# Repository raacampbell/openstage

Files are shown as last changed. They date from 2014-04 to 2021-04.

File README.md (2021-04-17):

<h1>OpenStage</h1>
<i>Open source microscope stage controller</i>
<br />

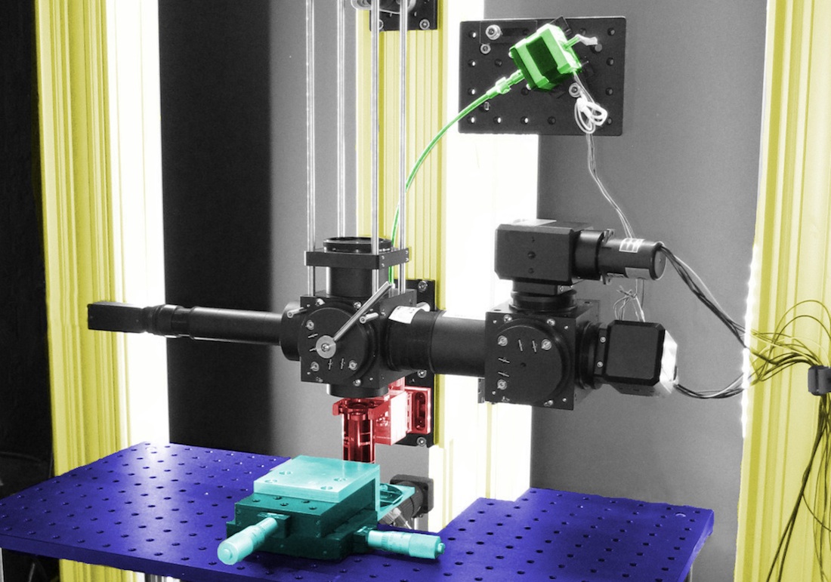
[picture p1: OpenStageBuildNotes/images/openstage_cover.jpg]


OpenStage is a hardware and software solution for cheaply motorizing a microscope stage. The system is accurate enough even for demanding tasks, such as fine focus operations on a 2-photon microscope. The characteristics of the system and important build information are described in our <a href="http://www.plosone.org/article/info%3Adoi%2F10.1371%2Fjournal.pone.0088977">PlosONE paper</a>. We achieved absolute unidirectional positioning accuracy and repeatability better than 0.1 μm in Z. Bidirectional positioning accuracy is in the range of 0.5 μm to 0.75 μm in Z. Positioning repeatability in X and Y is better than 1 μm. Minimum incremental motion is 0.04 μm in Z and 0.1 μm in X and Y. These values compare favorably to many commercial actuators costing several times as much as our system.

Our system costs roughly $1000 for three axes (controller + motors + motor coupling hardware). Up to four axes are possible. Commercial solutions cost in the region of $5,000 to $10,000. None of these costs include structural components such as bread-boards, linear translation stages, construction posts, etc, since all of this hardware is required no matter what motor solution is used. The breakdown of the costs is as follows:

* Motors and couplers are $100 to $200 per axis.
* Costs for micrometers, which act as the gear mechanism, are $80 to $150 per axis.
* A 4 axis controller unit can be assembled for under $500.

The cost savings come from the fact that we are using regular stepper motors instead of expensive linear actuators or servos. Further, the gears in our system are micrometers, which are easy to source and can even be bought at a discount from E-Bay. The main trade off compared to commercial systems is bulk, since connecting a stepper motor to a micrometer requires a relatively long (at least 8" or so) flexible shaft. However, if you can find a suitable leadscrew or rack and pinion gear as a substitute for the micrometer then the system will become more compact. A second trade off is that the controller unit does not have a feedback mechanism (encoders) for tracking position; position is inferred by counting the number of steps taken by the motors. In practice, this is not an issue as a properly assembled stage that is not driven beyond its operating limits will not lose position. Our system has maintained very high accuracy with zero maintanance. 

The stand-alone controller is based around an Arduino Mega. You can also build a single-axis controller around an Arduino Uno for under $100, but this can't accept a PS3 gamepad as there isn't sufficient SRAM on this device. The controller communicates with a PC via serial or virtual serial (USB) ports. An external LCD display and hand-held controller can also, optionally, be added. There is a PCB into which all components can easiliy be connected. The PCB was redesigned in Dec 2020 so that it's possible to construct it without obsolete SparkFun parts.  This verision of the PCB <a href="https://oshpark.com/shared_projects/8WlR0lh0">here</a> is no longer current. 

## Citing and Contact
Please do get in touch if you find this project useful or have used it in a publication. I'd love to hear from you!

## Updates

* *Arduino Mega ADK* - Users report that if the <a href="https://www.arduino.cc/en/Main/ArduinoBoardMegaADK">Arduino Mega ADK</a> is used, the project will run out of the box without the USB host shield.
* [Bluetooth gamepad connection details](https://github.com/raacampbell/openstage/issues/11#issuecomment-300612226)

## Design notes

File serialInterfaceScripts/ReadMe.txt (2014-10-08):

MATLAB and Python code examples for controlling OpenStage using the serial port commands. 

2014/04/08
Add *simple* LabVIEW VI for moving the stage.

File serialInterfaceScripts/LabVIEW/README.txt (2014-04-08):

This is a *very simple* LabVIEW VI for moving stage. Needs to be
expanded in order to become truly useful. Only sets a
position. Doesn't read one back.

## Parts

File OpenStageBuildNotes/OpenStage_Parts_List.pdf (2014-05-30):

* OpenStage PCBs can be manufactured relatively cheaply by SeeedStudio or OSH Park. Seeed has a minimum order of 5 units and OSH a minimum of 3. Seeed works out slightly cheaper in absolute terms and much cheaper per board. Listed price is roughly the cost for one OSH board. We may have boards in stock or may be able to split costs with you. If not, you're looking at around $120 to $170 for the minimum
bulk purchase.
TOTAL | 296.492
Description | Purpose | Quantity | Price Each (USD) | Sub-Total | Supplier | Part ID | | In addition, you will need a PSU that is suitable for driving your motors. It should be between 11V to 30V. Some possibilities are listed below.
Custom OpenStage PCB* | Main board | 1 | 50 | 50 | Seeedstudio or OSH Park
CUI V7809-1000 DC/DC Regulat | Produce 9V 1A DC | 1 | 7.81 | 7.81 | Digi-Key | 102-1717-ND
10uF 16V Cap | Filter for regulator | 1 | 0.48 | 0.48 | Digi-Key | 587-1376-1-ND | | Name & specs | Supplier | Part ID
10uF 50V Cap | Filter for regulator | 1 | 0.94 | 0.94 | Digi-Key | 587-3167-1-ND | | Mean Well 24V 4A. Will need jack. About $60 | Mouser | 709-CLG100-24
| | | | | | | | CUI Inc. 24V 2.7A. About $17 | Digikey | T1121-P5P-ND
5k Trim pot | LCD contrast | 1 | 0.98 | 0.98 | Digi-Key | 3362U-502LF-ND
Female DB9 connector | Motor connections | 2 | 3.14 | 6.28 | Digi-Key | 609-1485-ND
Male DB9 | PC serial port connection | 1 | 2.87 | 2.87 | Digi-Key | 609-1479-ND
Piezo buzzer | Audio indicator | 1 | 0.73 | 0.73 | Digikey | 445-2525-1-ND
ADM232 RS232 to Tx/Rx | Convert TTL <-> RS232 | 1 | 2.59 | 2.59 | Digi-Key | ADM232AANZ-ND
0.1 uF 50 V axial caps | Convert TTL <-> RS232 | 5 | 0.25 | 1.25 | Digi-Key | 399-4454-1-ND
Board-mount BNC connector | For *optional* debugging info (pulse waveforms) | 4 | 3.9 | 15.6 | Digi-Key | A32263-ND
Switch | Power switch | 1 | 3.85 | 3.85 | Digi-Key | CKN5001-ND
Power entry jack (24V 5A) | Input power to board | 1 | 1.16 | 1.16 | Digi-Key | CP-002AH-ND
0.5" M/F stand-off | LCD support post | 4 | 0.72 | 2.88 | Digi-Key | 8401K-ND
male 16 pos strip header | To connect PCBs to main board | 10 | 0.577 | 5.77 | Digi-Key | 609-3287-ND
female 1x16 strip header | LCD connector | 1 | 1.22 | 1.22 | Digi-Key | S7014-ND
female 1x6 strip header | USB host shield | 2 | 0.7 | 1.4 | Digi-Key | S7039-ND
female 1x8 strip header | USB host shield | 2 | 0.89 | 1.78 | Digi-Key | S7041-ND
female 1x2 strip header | Quadstepper power input | 1 | 0.5 | 0.5 | Digi-Key | S7035-ND
female 1x3 strip header | Quadstepper motor outputs (to be cut) | 10 | 0.384 | 3.84 | Digi-Key | S7036-ND
female 2x18 strip header | Quadstepper logic inputs | 1 | 1.41 | 1.41 | Digi-Key | S7112-ND
male 2x18 strip header | Quadstepper & Mega logic connections | 2 | 1.94 | 3.88 | Digi-Key | S2021E-09-ND
female 2x3 strip header | Mega ICSP | 1 | 0.82 | 0.82 | Digi-Key | S7106-ND
Jumper | Bypass R1 to LCD if it's not needed | 1 | 0.1 | 0.1 | Digi-Key | 3M9580-ND | You could also skip this and short the connections with a soldered wire
20k resistor | pull-down resistors for button | 3 | 0.05 | 0.15 | Digi-Key | RMCF1206JT20K0CT-ND
Indicator led | Indicate motor activity and serial port activity | 6 | 0.16 | 0.96 | Digi-Key | C5SMF-RJS-CT0W0BB2CT-ND
2.74 k ohm resistors | Current limiting resistors for LEDs (dim) | 8 | 0.1 | 0.8 | Digi-Key | 311-2.74KFRCT-ND | Choose this | There will be spare resistors (they're easy to lose)
300 ohm resistors | Current limiting resistors for LEDs (bright) | 8 | 0.034 | 0.272 | Digi-Key | RMCF1206JT300RCT-ND | Or this
300 ohm resistors | Current limiting resistors for debugging connectio | 10 | 0.034 | 0.34 | Digi-Key | RMCF1206JT300RCT-ND
N-channel power MOSFET | reverse polarity protection | 1 | 2.45 | 2.45 | Digi-Key | NP90N06VLG-E1-AYCT-ND
4-40 hex nut | to secure LCD stand off to main board | 4 | 0.15 | 0.6 | Sparkfun | PRT-10232
4-40 1/4" screws (10 pack) | to secure LCD to stand off | 1 | 1.5 | 1.5 | Sparkfun | PRT-10453
Quadstepper | Stepper motor driver board | 1 | 65 | 65 | Sparkfun | ROB-10507
Arduino Mega 2560 | Microcontroller | 1 | 59 | 59 | Sparkfun | DEV-11061
USB Host Shield | Interface with PS3 gamepad | 1 | 25 | 25 | Sparkfun | DEV-09947
20x4 LCD character display | Reports stage position, etc | 1 | 18 | 18 | Sparkfun | LCD-00256
Pushbutton | *OPTIONAL* reserved for future use | 2 | 0.5 | 1 | Sparkfun | COM-9190
USB cable | Connect PS3 controller to USB host shield | 1 | 3.95 | 3.95 | Sparkfun | CAB-11301
PS3 Game pad | For stand-alone stage control | 1 | 34 | 34 | Amazon | B0015AARJI
Wago 233-0506 6 pos term. block | For *optional* debugging info (direction, and pin1 | 1 | 3.16 | 3.16 | Newark | 79K2052
| | | | 0
M/M 10ft DB9 | Cut in half, providing 2 5ft cables to drive 4 motor | 1 | 9.99 | 9.99 | Cables2Go | #9449
F/F 10ft DB9 | PC serial port connection | 1 | 9.99 | 9.99 | Cables2Go | #2694
| | | | 0

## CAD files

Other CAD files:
CAD_Files/motor_coupler.ipt
CAD_Files/stage_assy_micrometer_coupler.ipt

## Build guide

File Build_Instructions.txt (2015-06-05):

Stage Build Instructions

** Introduction

If you have not already done so, you should read our PLoS ONE paper that describes both the properties of our stage and provides general instructions on its construction. http://www.plosone.org/article/info%3Adoi%2F10.1371%2Fjournal.pone.0088977 This document provides more detailed information on exactly how to go about setting up a new stage.

** Setting up a new motor

  * * Do Not Connect Motors To Your Stage Until You Have Tested The Assembled Controller * *

The first thing you're going to want to do is verify that you can drive a single motor in a reliable manner. For example, the motor will return to its starting point when commanded to perform 10 full revolutions counter-clockwise then 10 fill revolutions clockwise. To get to this point, you will need to configure and upload the firmware, wire the circuit for you system, and finally issue serial port commands from a PC and observe the results.

The minimum parts you will need to achieve this are:
1. An Arduino. An Uno can be used for basic testing and is adequate for simple single-motor stages. Even if you will ultimately use a Mega, you can start testing on an Uno.
2. A stepper motor driver board. OpenStage expects a Big Easy Driver or Quadstepper from Sparkfun. Other driver boards might have different input pins (e.g. different micro-stepping pins) and so might require minor re-writes of firmware. If you stick to Sparkfun's boards you'll definitely not need to do this.
3. A power supply adequate for your motor. A lab power supply with a current reading is useful but not critical.
4. A USB cable and hook-up wire to connect your prototype system.
5. Masking tape, lab tape, or similar.

A. Installing the firmware on the Arduino

You will need to install the AccelStepper library (http://www.airspayce.com/mikem/arduino/AccelStepper/). If you already have the library, make sure it's the latest version. There was a bug prior to v1.37 that introduced errors in bidirectional motions.

The "OpenStage" directory contains the firmware. The firmware is divided up across multiple source files. The file which begins "c_userSettings" and ends in ".ino" is the one which contains the user-specific settings which you will need to modify. More than one example file is included and these end in ".BAK" Choose the example that most closely resembles your use scenario. Rename it so it ends in ".ino" Read through the settings file and modify the settings as needed. There must be only one c_userSettings*.ino file in the directory. The .BAK files are ignored during the compile process and can be left in the same directory as the other files. You might want to set up the system so that serial port commands are delivered via the virtual serial port (Arduino programming port), as this initially is easier. The Mega has hardware serial ports that can be used for delivering stage motion commands. The advantage of using these is that you can deliver de-bugging messages to the Arduino IDE's serial port viewer via the USB. Once you're satisfied with the settings, upload the firmware to the Arduino via the IDE.

B. Wire the system

Wire up the system based upon the pin definitions you've chosen when you filled in the settings file. Don't forget to wire up the micro-stepping pins. Hook up the motor to the driver board. Set the current-limiting potentiometer on the driver board to the lowest setting and power up the board. If the chip on the driver board gets hot then you've turn the pot the wrong way.

C. Communicate with the stage.

Here it is assumed you are using MATLAB and communicating via USB. There are also Python functions and these should work equivalently, although they haven't been well tested. Note the ID of the serial port the Arduino is listening on: the port identity is listed at the bottom right of the Arduino IDE (assuming you have successfully transfered a program to the Arduino). Open the connectOpenStage.m file and replace the existing port name with your port. Save and close. Issue the OS_beep command. You should see the serial communications light flash on the Arduino, but will not hear a beep unless you have wired up a buzzer. Now let's see if the motor moves.

Attach a piece of tape to the spindle (like a little flag) to act as a clear visual indicator that the spindle has rotated. We will begin by asking the spindle to rotate by 360 degrees. You want to make sure the spindle always returns to its start position. The gear ratio value you entered in the settings file defines the number of microns per revolution, thus if you ask the motor to travel this many microns you should get a 360 degree rotation. For example, a standard 100 turn per inch micrometer will advance 635 microns in one revolution. Thus, the following motion command executes repeated 360 rotations:

while 1, OS_goto(635,1); pause(1), end

Issue that command, replacing "635" with your value. You can break out of that loop with ctrl-c. You will likely see no motion initially since you have turned down the current-limiting potentiometer. Slowly increase the current with the potentiometer and watch the motor. Usually when the motor is operating at its quietest, the current setting is near-optimal. Then add another 1/10th of a turn or so as a buffer (the amount of current needed will increase when the motor is running under load). Adding more current can reduce the ability of the motor to accelerate rapidly to full speed. If you do not see 360 degree rotations then check your gear ratio value, check that the micro-stepping wires are hooked up, and make sure that you're not driving too much or too little current to the motor. Do not proceed until you're getting smooth 360 degree motions. If you're still having problems, check you're moving in half or quarter steps (OS_stepSize.m) and that the speed is reasonable (OS_moveSpeed). With some motors, moving smoothly at full steps may be difficult. So you may well be able to accelerate much faster, reach higher speeds, and work with higher currents (higher torque) if you avoid full steps. Note that your motor has a maximum RPM value. If you go above it or accelerate too fast to reach it, then it will stall or partially stall and you will lose steps. The result of this is that spindle will fail to rotate by 360 degrees and will repeatedly under-shoot. If you're having problems, issue OS_getInfo and check the max RPM you are asking your motor to reach.

You can check that the motor returns to the start value by observing the location of the piece of tape with respect to a nearby fixed object. One strategy is to start off the motor so the tape is aligned with one of the four mounting screw holes. You can spy the tape from in front and align it by eye with the screw hole. Then issue the 360 degree rotation commands and check that it always returns to the same place. This might sound inaccurate, but in practice you can pick up errors of under a degree using this technique. A 1 degree error with a gear ratio of 635 works out to 1.76 microns. It's easy to see what is the smallest angular discrepancy you can pick up by eye: set the system to 1/16th steps and issue small back and forth motions. Find the smallest easily detectable motion. If you want to get fancy, you can attach a protractor to the spindle and set up a fixed pointer. It should be easy to see discrepancies of under half a degree in this manner.

D. Trying different speeds and step sizes

Now you want to check that the motor continues to perform well at faster speeds. Set your step size to full steps (OS_stepSize(1)). You can confirm this worked with OS_getInfo. Check the motions again. Try faster motion speeds with OS_moveSpeed: calling this with no arguments reports the current speed. Giving it a argument sets the speed. You can keep going up in speed until your motor stalls. OS_getInfo will tell you the max RPM you're asking of your motor. This should match roughly with the value on the spec sheet. If you're stalling or skipping well below that value (i.e. half or quarter of that value) then check your motor current (too high or too low is bad) and consider a more gentle acceleration regime. Try also going to half steps, as this often leads to smoother motions and less skipping.

E. Test back and forth motions.

Choose some reasonable settings at which you know the motor performs well. Reset the Arduino and start issuing absolute motion commands. e.g. OS_goto(6350,'a') causes the motor to advance 10 full rotations in one direction, then OS_goto(0,'a') sets it back to the starting point. You can issue much smaller motions, too, such as 10 microns. Try a bunch of different motions in various directions. When you finally issue OS_goto(0,'a'), it should always return back to the starting point.

One thing you could try is to issue the following code:

OS_goto(0,'a',1); for ii=1:250, OS_goto(round(rand*2000),'a',1), pause(0.1), end; OS_goto(0,'a',1);

Go have a coffee and come back. The spindle will execute 250 random motions then return its starting position. If it can do that, you should be good to go. Remember to start it at a location where you have a reference. You can make the current position the zero location by executing `OS_zero;`

** Necessary Hardware for a three-axis stage
The easiest way to get up and running is to use an Arduino Mega 2560. This unit has enough IO pins to handle multiple axes, an LCD display, etc. An Arduino Due is not suitable since it is not currently compatible with the USB Host Shield we use to read the PS3 gamepad, which is our input device. The same goes for ChipKit boards. So unless you want to write your own game-pad driver (contact me if you do), you're stuck with the Mega.

You can use only the serial port as the input device, but the PS3 dual shock is a great way of interacting with a three axis stage. This plugs into a USB Host Shield. I used the SparkFun version of the USB shield. If you don't stack the shield you will have access to more of the Mega's pins. To wire the devices in this way you will need to do the following:
    a. Connect pin 7 to reset on the shield.
    b. Connect reset on the shield to reset on the Mega.
    c. Connect GND and VIN on the shield to GND and VIN on the Mega.
    d. Connect pin 13 on the shield to pin 52 on the Mega.
    e. Connect pin 12 on the shield to pin 50 on the Mega.
    f. Connect pin 11 on the shield to pin 51 on the Mega.
    g. Connect pin 10 on the shield to pin 53 on the Mega.
    h. Connect pin 10 on the Mega to pin 53 on the Mega
This wiring diagram is also shown in our paper.

The libraries to interface with the DualShock are found here: https://github.com/felis/USB_Host_Shield_2.0. You can also install via the library manager in the Arduino IDE. You will note that there are drivers for XBox and Wii controllers also. However, our code assumes a DualShock. You can plug the controller directly into the USB shield with a mini USB cable or you can use Bluetooth if you can find a compatible dongle.

  - Per axis hardware:
      a. one Big Easy Driver (or similar, see Sparkfun). The motors have two pairs of
        leads called A and B. The letters A and B are also marked on the Easy Driver.
        Inverting the connections of the motor to the driver (i.e. connecting the A
        lead pair to B and vice versa) will invert the direction of rotation of the
        motor. Connect as required to get the stage moving in the correct direction
        according to button presses. The micro-controller software knows only stage
        direction, not how it maps onto left and right. You determine that according
        to how the motors are wired to the controllers. The micro-stepping pins on all
        axes are wired together.
      b. one micrometer. We use regular Thor 50 TPI for X and Y and a Newport
        HR-13 (100 TPI) for Z. Obviously a translation stage is needed too.
        Choose a stage from Newport or Thor according your needs.
      c. one flexible coupler. (https://sdp-si.com/eStore/Catalog/Group/484)
        Choose operating torque over about 6 lb-in to minimise back-lash.
        We use 8" couplers for X and Y and a 10" coupler for Z.
      d. one stepper motor. We used Vexta motors sourced from orientalmotor.com
        We use Vexta PK243M-02BA for XY and PK243M-01BA for Z.
      e. Machined male/female adapters to attach the flexible couplers to the micrometer
        head and stepper motor shaft (if shaft is not 1/4").

  - Misc: You will also need a power supply for the motors (usually 24V). The Arduino
  will need eternal a power supply (USB isn't enough) if you're using the USB host shield.
  You can either use a second PSU or a voltage regulator to drop the motor PSU down to 9V
  or so. Finally, a Sparkfun RS232 Serial Shifter is needed if you want to interface the
  controller with a PC via the serial port (not virtual serial).

* Usage instructions:
  The DualShock controls the stage in the following ways:
  1. Left hat-stick for X and Y. Right hat-stick up/down for Z. Right hat-stick left/right
     does not do anything.
  2. D-pad executes single motion steps in X and Y motions. D-pad plus Triangle performs
     fixed-step motions in Z.
  3. Shoulder buttons (L1 and R1) cycle through four different speed modes. Selected speed
     mode indicated by LEDs on the DualShock. 1 is slow and 4 is fast. See global variables
     below for speed values these select. Speed modes influence hat-stick motions and D-pad
     fixed speed motions.
  4. Pressing one of the four right-hand buttons stores the current stage location. Storage
     is signaled by two beeps. Double-clicking the button will cause the stage to move to the
     stored location. All four buttons default to the position of the stage on reboot.

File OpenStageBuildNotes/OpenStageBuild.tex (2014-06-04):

%%%%%%%%%%%%%%%%%%%%%%%%%%%%%%%%%%%%%%%%%%%%%%%%%%%%%%%%%%%%%%%%%%%%%%%
%%%%  Load the document class and packages                         %%%%
%%%%%%%%%%%%%%%%%%%%%%%%%%%%%%%%%%%%%%%%%%%%%%%%%%%%%%%%%%%%%%%%%%%%%%%
\documentclass[11pt]{report} %LOAD THE DOCUMENT CLASS
%\documentclass[a4paper]{report}
%\usepackage{epsfig}            % to insert PostScript figures

\usepackage{graphicx}
\include{srctex}               % For Latex inverse searc
\usepackage[bf,footnotesize]{caption} % make captions small and label bold
\usepackage{hyperref}
\usepackage[letterpaper,margin=3cm,tmargin=2.75cm,bmargin=3cm]{geometry} 

%%%%%%%%%%%%%%%%%%%%%%%%%%%%%%%%%%%%%%%%%%%%%%%%%%%%%%%%%%%%%%%%%%%%%%%
%%%%  Setup a default path to search for graphics                  %%%%
%%%%%%%%%%%%%%%%%%%%%%%%%%%%%%%%%%%%%%%%%%%%%%%%%%%%%%%%%%%%%%%%%%%%%%%
\graphicspath{
              {images/}
}

\setcounter{secnumdepth}{-1} 
\begin{document}

\section{Introduction}
These are the instructions for building the OpenStage microscope stage controller based around a Rev 2 PCB. The Rev2 board is a prototype and contains some mistakes that you will have to work around. None of these mistakes are show-stoppers, they just result in some cosmetic kludges. \textbf{Read the whole way through this guide before you start soldering.} Think before you solder: you are the first (or one of the first) to build this thing so there may be mistakes in the guide. Please report your experience and any errors you find. Some steps have various solutions: choose the one that works best for you. The Rev 2 board has the following issues, all of which have solutions\footnote{Your board will likely come with the power switch holes drilled out and a serial port connector correctly wired}:

\vspace{2em}

\begin{tabular}{|p{5.5cm}| p{9cm}|}
\hline
Issue & Solution \\
\hline
\hline
LCD header is inverted & Connect LCD to PCB via a ribbon cable, to flip the lines left/right \\
\hline
Serial comms socket is inverted & snip off socket pins 1 and 4. Solder socket into place. Connect solder pads at positions 1 and 5 and also at positions 2 and 4. \\
\hline
Power switch drill holes too small & Drill out (carefully!)\\
\hline
Top left LCD spacer drill hole too close to jumper & Either don't use this spacer or short jumper using solder or wire, this will provide enough room to screw in a spacer. \\
\hline
Some drill holes for case mounting overlap with mounted components & User other drill holes--there are loads. \\
\hline
Motor serial connectors are a little closer to each other & Serial sockets that plug into the connectors do fit side by side (just!)\\
\hline
Connections from Quadstepper motor outputs to Openstage PCB are a bit crap. & 
I'm looking for suggestions! \\
\hline
\end{tabular}

\clearpage

Figure~\ref{frontback} shows the bare PCB, as it looks like before you start. Figure~\ref{finished_1} shows roughly what the board will look like when it's finished, with the components installed. Optional buttons near the top of the front of the board haven't been installed here. The LCD display will \textit{not} just slot into the header, unfortunately, as the connections are backwards. You should probably solder the wiring for the LCD display right at the end. 

\begin{figure}[!ht]
\centering
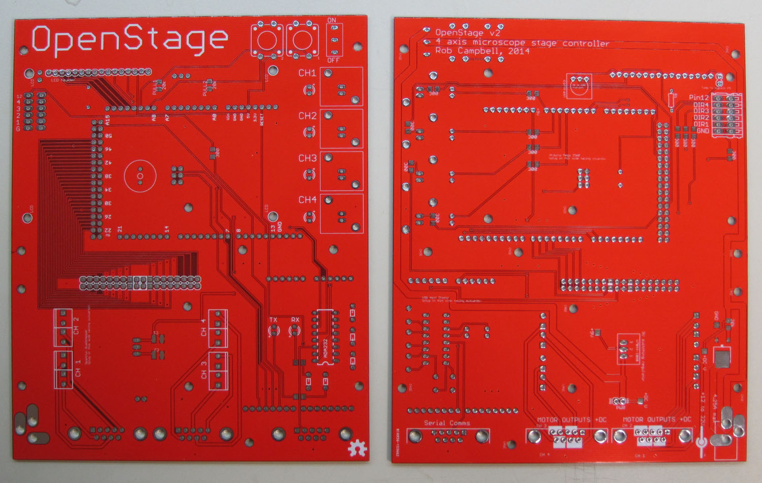
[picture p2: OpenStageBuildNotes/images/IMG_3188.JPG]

\caption{Front (left) and back (right) views of the bare PCB.}
\label{frontback}
\end{figure}

\begin{figure}[!ht]
\centering
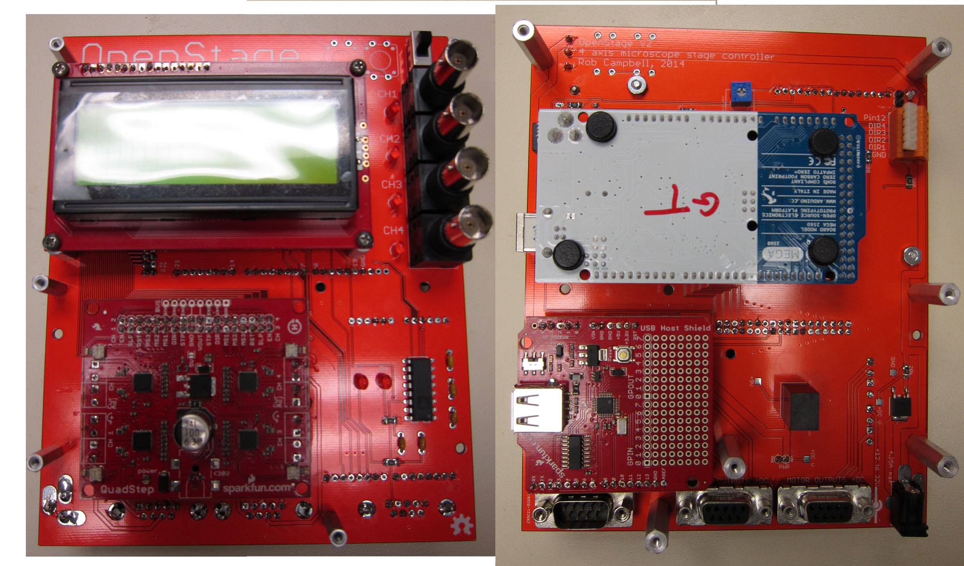
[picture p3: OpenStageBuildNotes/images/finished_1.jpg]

\caption{Front (left) and back (right) views of the finished PCB.}
\label{finished_1}
\end{figure}

\clearpage

\section{Getting power to your board}
The first thing we'll do is hook up the components related to powering the board. You'll install the main power switch, input jack, the 9V regulator which powers the Arduino and USB host shield, and the MOSFET that is used for reverse current protection. 

Install the power switch (Fig.~\ref{switch}) so it's facing frontwards (i.e. the solder will be applied to the \textit{back} of the board). In Rev 2 boards the drill holes are too small for this switch and they've been expanded to allow the switch to fit. Solder will not take on the lower, unused, switch connection. This is not a problem. Next solder the power jack, MOSFET, and 20k resistor to the back of the board (Fig~\ref{switch}). The MOSFET and resistor are surface mount, so all the soldering is to the back face of the board. The power jack is through hole, so it's inserted into the back face and you solder to the front face. 

\begin{figure}[!ht]
\centering
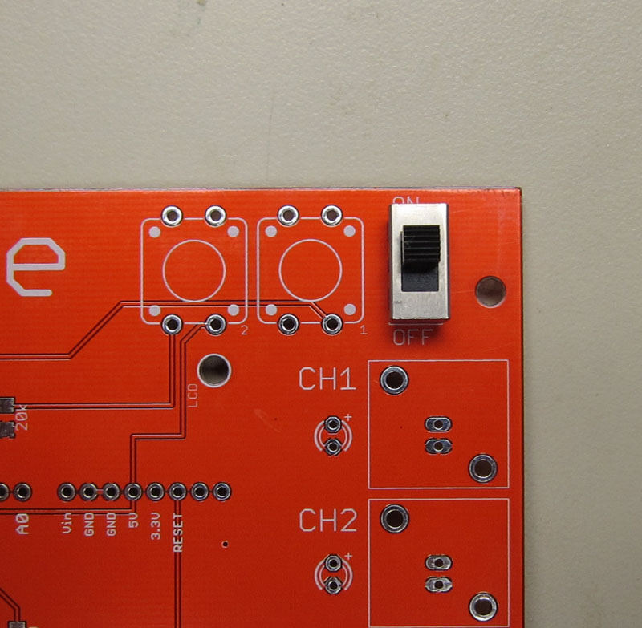
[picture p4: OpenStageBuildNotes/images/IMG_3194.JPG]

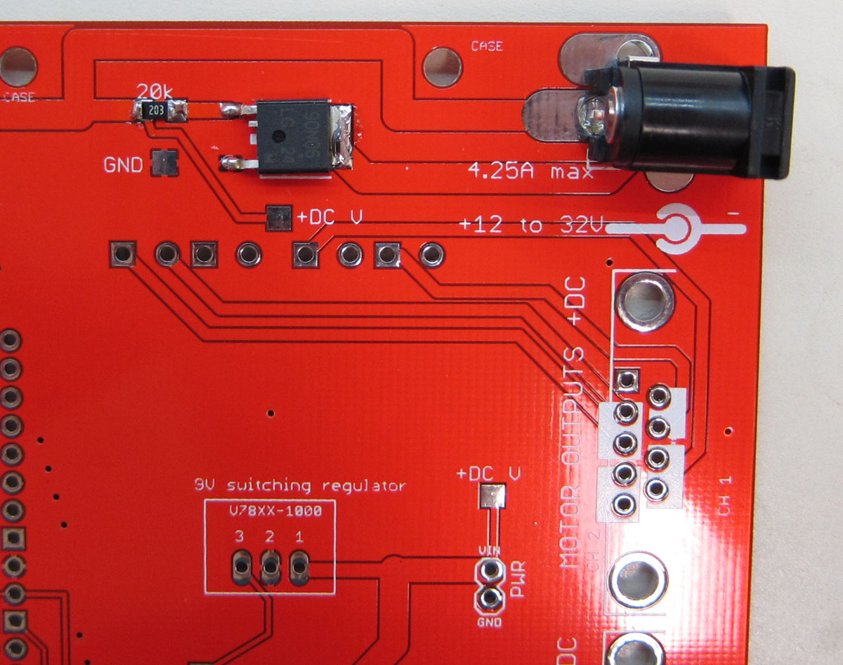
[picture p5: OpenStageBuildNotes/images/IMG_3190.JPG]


\caption{Power switch (left). Power jack and reverse polarity protection (right).}
\label{switch}
\end{figure}

\clearpage

\section{Soldering small surface mount components}
Soldering the surface mount resistors is not too tricky once you have the technique down. First apply a little solder to one pad (Fig.~\ref{onePad}) then solder resitor to this pad with the aid of forceps (Fig.~\ref{forceps}). Finally, solder the remaining pad (not shown). 

\begin{figure}[!ht]
\centering
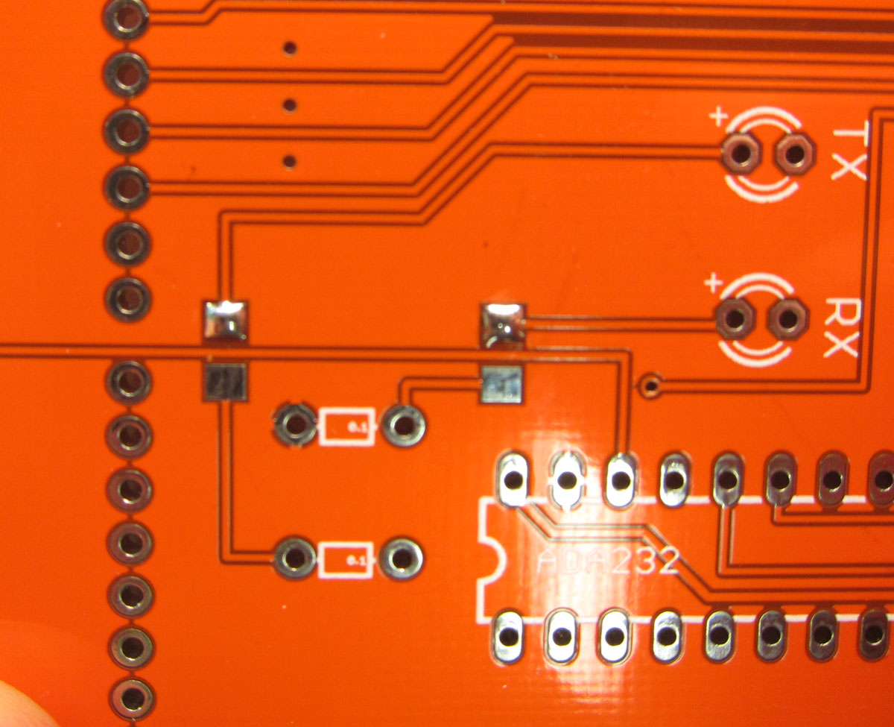
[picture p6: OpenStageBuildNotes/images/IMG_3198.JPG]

\caption{Solder applied to one pad in preparation for soldering a resistor in place. Image shows two pairs of reistor pads. Solder has been applied to the upper pad of each pair. }
\label{onePad}
\end{figure}

\begin{figure}[!ht]
\centering
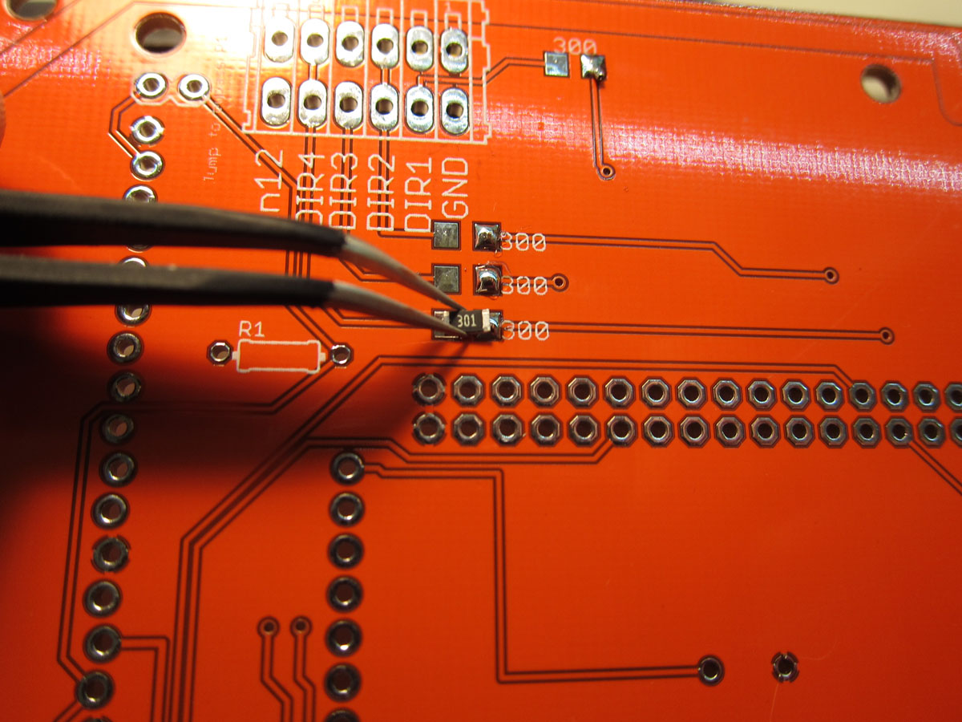
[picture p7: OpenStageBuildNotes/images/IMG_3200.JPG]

\caption{Rest resistor on one pad. Keep in place with forceps. Apply solder.}
\label{forceps}
\end{figure}

\clearpage

Solder the two surface-mount capacitors to the front of the board (Fig.~\ref{9V}, left). The capacitor with the higher voltage rating goes on the input side of the regulator (the lower pair of pads, nearer the serial ports). Then solder into place the 9V regulator to the rear of the board (Fig.~\ref{9V}, left). The regulator has a dot indicating which pin is number 1. 

\begin{figure}[!ht]
\centering
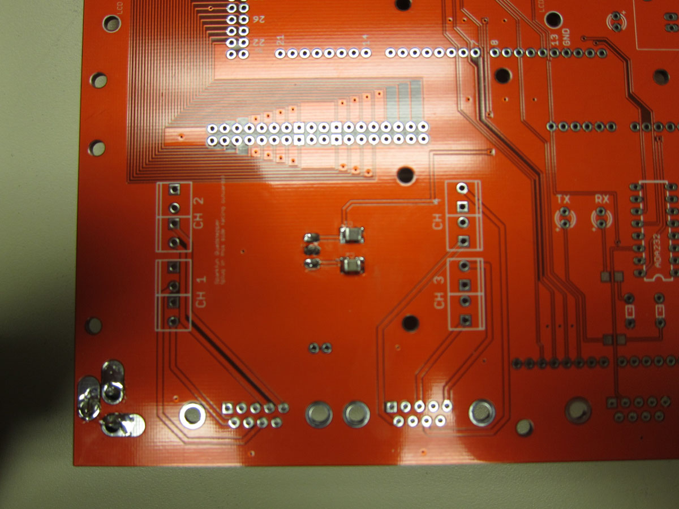
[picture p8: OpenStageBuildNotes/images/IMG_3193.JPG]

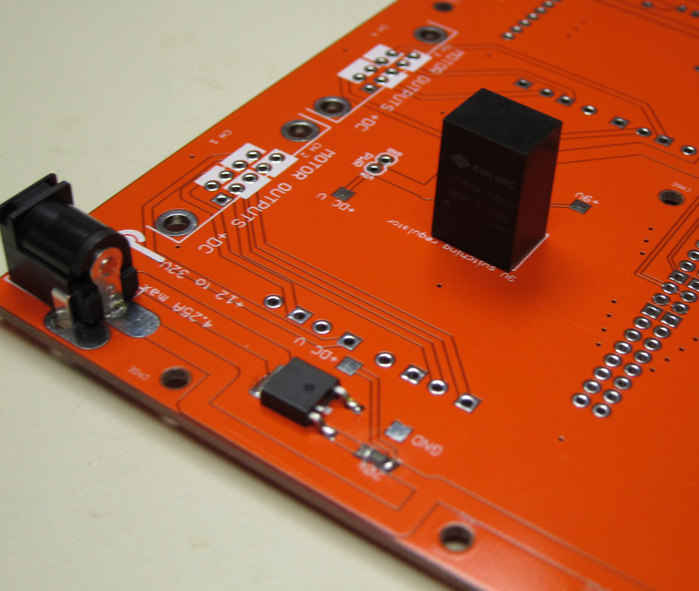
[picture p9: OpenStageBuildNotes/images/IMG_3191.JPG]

\caption{Capacitors for 9V regulator (left). 9V regulator (right).}
\label{9V}
\end{figure}

\clearpage

\section{Testing the power}
At this point you have enough circuitry on-board to check that the power is being distributed correctly. Apply the probe leads across to points which ought to be supplying the full input voltage. The inputs to the QuadStepper are a good place (Fig.~\ref{power}, left). In the example images, we're using a 24V supply. We measure 24V when we do this. This should be under the control of the board's power switch. Next check that you get 9V after the regulator. You can use the 9V test pad and any ground connection (including the Quadstepper's ground you previously used to measure the full input voltage). This should read close to 9V (Fig.~\ref{power}, right). Finally, you can switch the polarity of the input jack if you wish. You should no longer be able to pick up a voltage. This indicates that the MOSFET-based reverse polarity protection is working as expected. 

\begin{figure}[!ht]
\centering
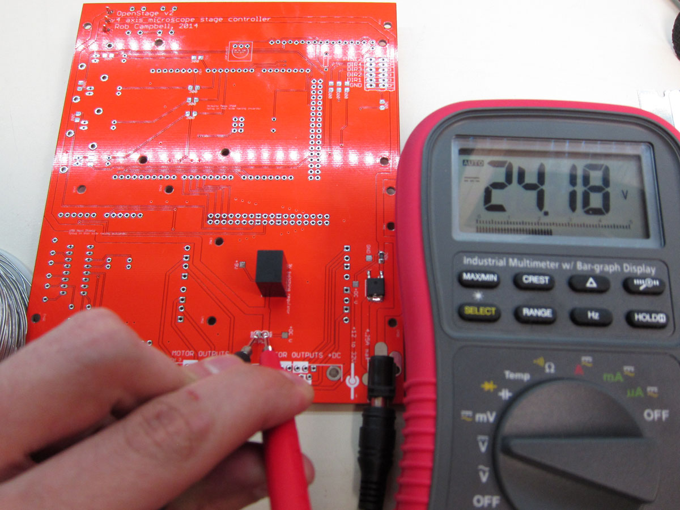
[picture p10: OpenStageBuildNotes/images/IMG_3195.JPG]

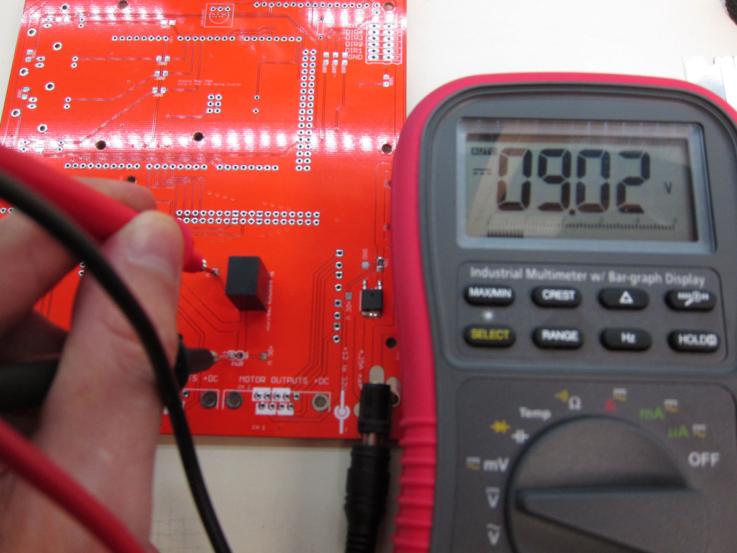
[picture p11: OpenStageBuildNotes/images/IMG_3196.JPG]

\caption{Measuring input voltage (left), in this case 24V. Measuring output of 9V regulator (right).}
\label{power}
\end{figure}

\clearpage
\section{Attach small components}
Now is a good time to solder into place the smaller components. There are 15 resistors to attach. Six of these are current-limiting resistors for the indicator LEDs. If you want the LEDs bright then use a resistance of about 300$\Omega$. If you want them dim, then about 2500$\Omega$ to 3000$\Omega$ should do the trick. The remaining 9 resistors are current limiting resistors for the debugging lines; these are all 300$\Omega$. The buzzer is attached to the front face of the board. The ADM232 (Fig.~\ref{ADM232}) IC and associated capacitors attach to the front face of the board. Also shown in Fig.~\ref{ADM232} are the two indicator LEDs. These may have little `shoulders' on the pins that will prevent the LEDs from being fully inserted. If this is the case, you can clip away the shoulders. Insert the remaining 4 indicator LEDs. Attach the 5k$\Omega$ trim pot to the back of the board (Fig.~\ref{megaHeader}). Optionally, attach the Wago terminal connector for the debugging lines (Fig.~\ref{megaHeader}). 

\begin{figure}[!ht]
\centering
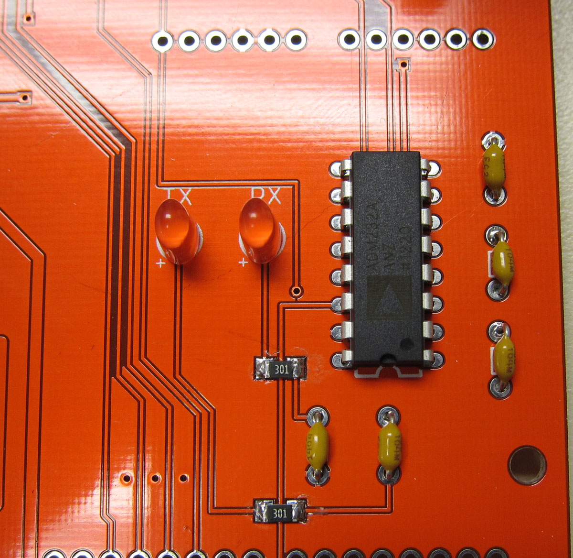
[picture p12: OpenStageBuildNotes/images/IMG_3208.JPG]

\caption{ADM232 serial comms IC and associated capacitors.}
\label{ADM232}
\end{figure}

\clearpage

\section{Soldering the headers for the Arduino and USB host shield}
This is the most tedious bit but it's also the easiest to get wrong. Make sure the headers go into the correct side of the board. Let's start with the Arduino Mega male headers (Fig.~\ref{megaHeader}). These should be on the back face of the board. The idea is to have the Mega facing inwards on the back face, as shown in Fig.~\ref{megaHeader}. You will likely have to cut the single male rows from a longer strip. Once you're done here, do the headers for the USB host shield (Fig.~\ref{usbHost}). This also attaches to the back face of the OpenStage PCB. In this case we've soldered female headers to the OpenStage board and male headers to the USB host shield. It work equally well the other way around. 

\begin{figure}[!ht]
\centering
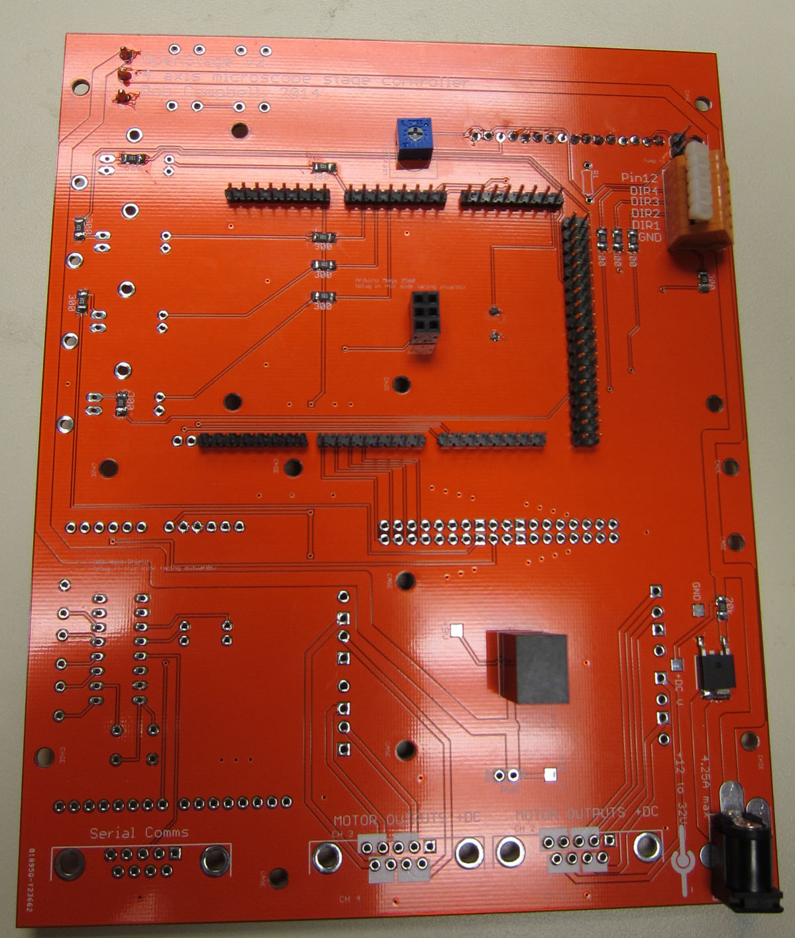
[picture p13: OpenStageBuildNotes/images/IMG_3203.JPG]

\caption{Shows Arduino Mega headers, trim pot, and Wago terminal block. Note that the middle 2x3 header for the Mega is female.}
\label{megaHeader}
\end{figure}

\begin{figure}[!ht]
\centering
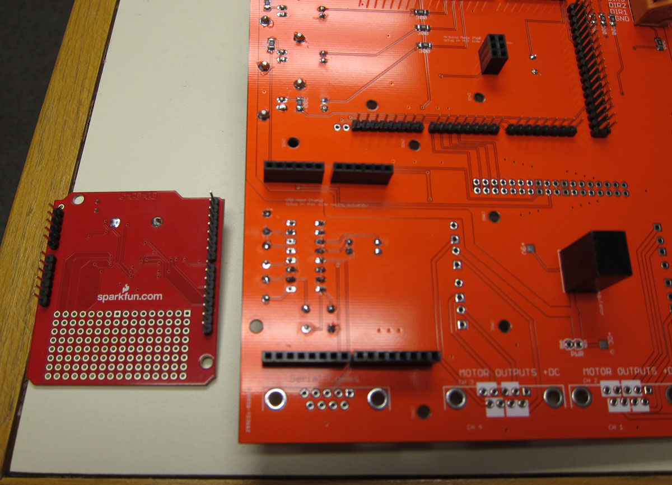
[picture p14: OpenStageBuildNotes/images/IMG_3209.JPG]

\caption{USB host shield shown with headers attached. }
\label{usbHost}
\end{figure}

\clearpage

\section{Hooking up the Quadstepper}
Connecting the Quadstepper is a little more involved. First of all, you'll need to remove its power input jack. This is surface mount so you easily can snip off at the four attachment points. Do this \textit{carefully} so you don't rip up any traces: one of the solder pads is part of a trace. If you do damage it, you'll have to bridge the gap with wire. This done, solder male headers to the underside of the newly-revealed 1x2 DC power connectors. Then attach male headers to the 2x19 strips. These are the digital control inputs for the motors. Again, these go on the \textit{underside} of the Quadstepper, so you can mount it facing outwards on the front of the OpenStage PCB (Fig.~\ref{finished_1}). Then solder the corresponding female adapters to the \textit{front} of the OpenStage PCB. 

The final step, the motor outputs, is a bit of an adventure. The pitch of these header holes is 0.15" and strip headers aren't available with this spacing. I've yet find a neat solution, so I present two options here. One, which allows you to easily remove the Quadstepper, is to attach male single pins to each motor output on the Quadstepper then cut 1x3 female adapters down to 1 pin and attach these to the OpenStage PCB. This looks like crap (Fig.~\ref{motoroutputs}, left), and you may need a glue gun get the female headers sitting properly before you solder them. Thus, an alternative is to solder the motor connections with short wires (Fig.~\ref{motoroutputs}, right). This looks nicer, but it means you can't get the Quadstepper off very easily. Given that there is no reason to remove it, the latter option might be the easier. Once you've done this, solder into place the two female DB9 sockets for the motor outputs. 

\begin{figure}[!ht]
\centering
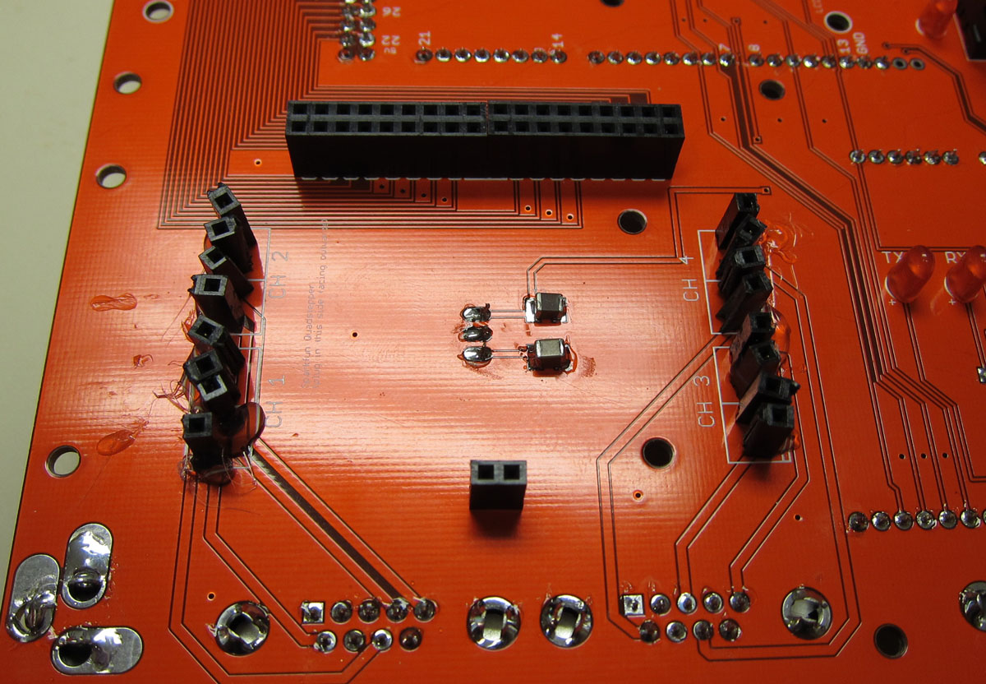
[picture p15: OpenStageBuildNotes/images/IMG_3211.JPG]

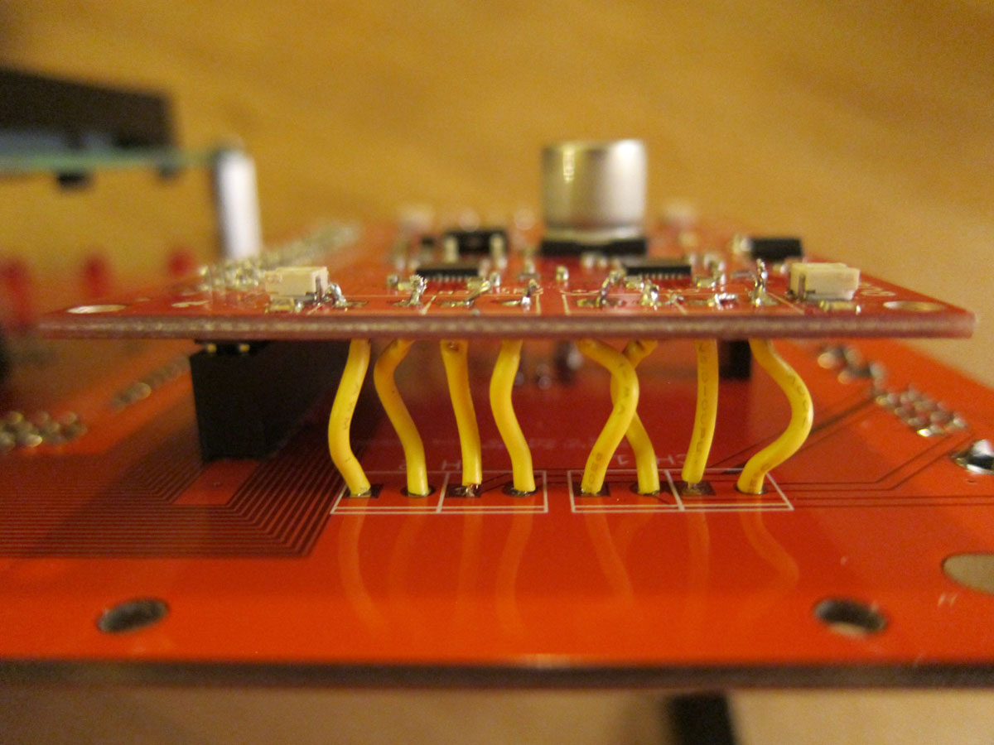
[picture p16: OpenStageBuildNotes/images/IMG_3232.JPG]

\caption{Quadstepper female headers on OpenStage PCB (left) or using wires (right) }
\label{motoroutputs}
\end{figure}

\clearpage

\section{Wiring up the LCD display}
Because this a Rev 2 board, the LCD display won't just slot into place with a male and female header. This is because the connection on the board is inverted. To get around this, the easiest thing is to use a ribbon cable to invert inputs. You want to have something that looks like Figure~\ref{ribbon}. There are a bunch of ways you could do that. In the images shown, I've soldered a male strip header to the back of the LCD display. The 16 wire ribbon is soldered directly onto those pins. The other side of the cable has a female header on it. This female header connects to a 90 degree male header on the back of the OpenStage board. You could equally well solder directly the LCD. See how much space you have and what works best for you. If you wish to attach the BNC connectors next to the LEDs, you could do this now. These BNC connectors allow you to monitor the step pulse trains going to the motors.

\begin{figure}[!ht]
\centering
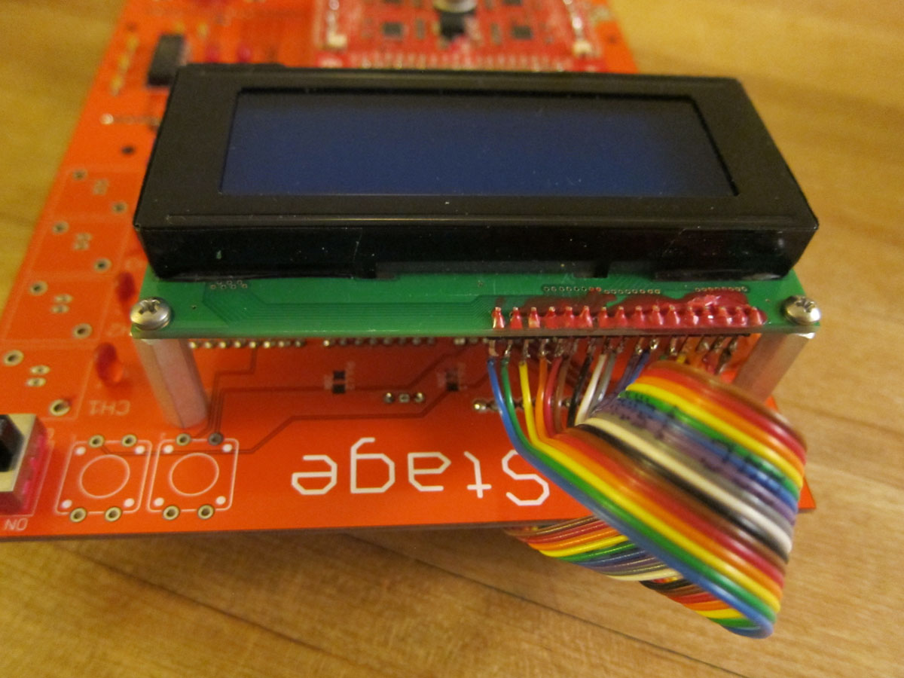
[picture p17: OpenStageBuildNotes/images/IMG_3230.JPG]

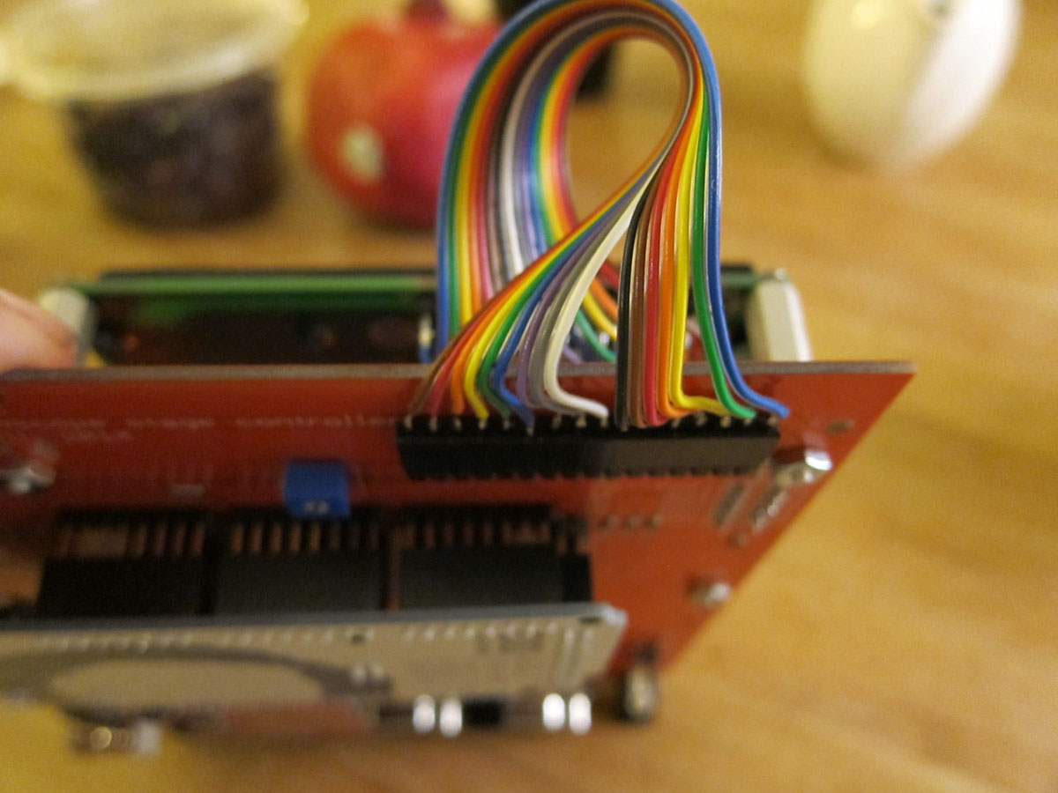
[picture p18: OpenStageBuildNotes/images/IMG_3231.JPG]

\caption{Using a ribbon cable to invert the LCD inputs.}
\label{ribbon}
\end{figure}

\clearpage

\section{Connecting the motors to the DB9 cables}
Get a M/M DB9 cable and cut in half. Strip and expose the leads. You will be using 4 or 6 wire stepper motors. 6 wire steppers will have one pair of wires that aren't connected to anything. Stepper have two sets of coils inside and each set of coils is connected to one pair of wires. Use your datasheet or a continuity tester to figure out which wires form a pair. If you have 6 wire steppers, you will need the datasheet to make sure you avoid using the middle wires from each coil. Each row on the female DB9 connectors is for one motor. On the bottom row, pins 6\&7 connect to one coil and 8\&9 connect to the other coil. On the top row, pins 5\&4 form a pair and pins 3\&2 form a pair. Pin 1 is unused. It doesn't matter which coil connects to which pair of pins, but switching the coils will switch the default motor direction\footnote{There will soon be a way of switching default motor direction in the user settings section of the source code firmware. Currently, the only way is to switch the wiring.}.

\section{Uploading the firmware}
The board should now be assembled. Plug in the Arduino Mega, USB host shield, and Quadstepper. If it's not already programmed, hook up the Mega to a PC and upload the OpenStage firmare from the Github page (\textit{https://github.com/raacampbell13/openstage}). You can download as a zip (easy) or clone the repository (if that's your thing). You will also need to download and install the Arduino USB Host Shield library (\url{<https://github.com/felis/USB_Host_Shield_2.0>}) and the AccelStepper library (\url{<http://www.airspayce.com/mikem/arduino/AccelStepper/>}).

If you haven't programmed an Arduino before, here's what you'll need to do. Download the Arduino IDE from \textit{arduino.cc}. Install the IDE. The source code for the OpenStage firmware is in the `\textit{OpenStage}' sub-directory from the Github repository. There are a bunch of source code files here. Unless you want to make significant changes to the firmware, you don't need to be concerned with most of this. All you care about is the user settings file. There are a bunch of different potential user settings files, depending on the desired configuration of the stage. We want the c\_userSettings\_MEGA\_PCB file. This file should have the extension `.ino'; if it has `.BAK', or any other extension, then rename the file. It should be called `\textit{'c\_userSettings\_MEGA\_PCB.ino'}. When you try to compile the firmware, the Arduino IDE simply concatenates the .ino files in the directory then compiles the resulting, larger, file. You don't want it to include any of the other c\_userSettings* files. So either delete them or make sure none of them end in .ino 

Now you're good to go! Open the file `\textit{OpenStage.ino}' in the Arduino IDE. When you do this, a new window will pop up and it will have about a dozen tabs. Each is a source file (.ino file) from the directory. Go to the tab called c\_userSettings\_MEGA\_PCB. If that tab doesn't exist, you didn't rename the file correctly. If there are any other tabs starting with `c\_' then you didn't remove or rename the extra settings files. If you have such issues, close the IDE and rename files to fix the problem. In the c\_userSettings\_MEGA\_PCB tab you can modify the user settings for your rig. You will want the LCD display and, presumably, the game pad, so don't alter the first three lines. If you want to communicate with the stage via the Arduino USB port, not a regular serial port, then change the value of controlViaUSB to 1. 

You will need to carefully set the `Microscope axis hardware definitions.' If you want three axes then leave the first bit of that section (up to `gear ratio') as is. What you likely will need to do is modify the gearRatio vector. Those numbers indicate the number of microns the stage will advance when the micrometer rotates revolution. e.g. The standard ThorLabs micrometers are 100 turns per inch; the imperial units advance 635 $\mu m$ per revolution and the metric ones 500 $\mu m$ per revolution. Each axis can have a different value, allowing finer motions for $z$, say. Similarly, you will need to define the number of degrees the stepper motors advance when they take a full step. Chances are you will have motors which are 1.8 degree (200 steps per revolution) or 0.9 degree (400 steps per revolution). Armed with these two pieces of information, OpenStage can determine its relative position in space with very high accuracy. 

The remaining parameters are less critical. They relate to things such as the speeds and step sizes that the PS3 game pad produces and the default speeds on each axis for PC-based control. Many of these settings can be altered via the serial port (see the serial port commands directory). You won't need to change the pin definitions at the end of the file. 

\section{Powering up!}
You're now ready to power up. Connect your power line and PS3 game pad. Hook up the motors (do not plug or unplug the motors with the power on). If you want computer control, hook up the USB cord or the serial port to your PC. To begin with, it might be sensible not to connect the motors to the rig. Attach little pieces of tape to the spindle to watch them move. Make sure the switch on USB host shield is set to `on'. Switch on OpenStage. You should see a `Booting...' message on the LCD display. The boot sequence should complete in about 5 seconds. Once it has booted you can control the stage using either a PC or the gamepad. 

The Quadstepper has 4 potentiometers, one for each motor. These control how much current is delivered to the coils. The power supply determines the voltage to the coils. If the current is too high the motors and the driver chips can run \textbf{very hot}. It shouldn't be necessary to run at high currents. Choose a low current at work your way up. You shouldn't need a heatsink on the motor. You might like to add a heatsink to the driver chips; again, however, this likely isn't necessary as they should be running cool. If the current is too low the motors will skip (see below).

\subsection{Control via gamepad}
The PS3 gamepad serves as a comfortable input device. The LCD displays current speed and position of each axis. The display is updated regularly, except at the fastest speed mode (see below) where it updates only at the conclusion of motion. 
The PS3 DualShock controller provides the following functionality:

\begin{itemize}
\item \textit{Analog control} of speed and direction for each axis is
  provided by the two analog sticks. The left stick controls X and Y and the right stick controls Z, and the 4th axis (z) if this is enabled. Larger stick displacements are mapped to higher motion speeds, making it easy to manually guide the stage at exactly the desired speed.
\item \textit{Fixed-size motion steps} are provided by the direction
  pad (D-pad). For instance,
  pressing the left D-pad button moves the stage one increment to the
  left. By default the D-pad controls X/Y motions; holding down the
  Triangle button whilst pressing up or down on the D-pad yields fixed
  step size motions in Z, with Triangle plus L/R yielding motions in z. 
\item The two shoulder buttons (L1 and R1) allow the user to cycle between 4
  different \textit{Speed Modes}. The selected speed mode influences
  both the maximum speed of analog stick motions and the size of the
  D-pad motion steps. Speed mode \#1 provides a nominal maximum speed
  of $3~\mu m/s$, \#2 is $25~\mu m/s$, \#3 is $100~\mu m/s$, and \#4 is
  $750~\mu m/s$. The size of the D-pad steps range from $3~\mu m$ to
  $50~\mu m$. Changing the speeds and motion steps sizes involves only
  trivial modifications to the source code (see above). The currently selected
  Speed Mode is indicated by the 4 LEDs on the DualShock. The stage boots in a low speed mode for safety reasons. 
\item The user can \textit{store} up to 4 locations and return to them
  later using the 4 right-hand buttons. Firmly press on a button for 1 second to store the current stage position. The controller produces an audible
  indication when a new location is stored. Return at any
  time to the stored location by double-clicking on the corresponding
  button. OpenStage returns to the stored position at maximum speed, as defined in the settings file. 
\end{itemize}

\subsection{Control via PC}
The Github repository contains a directory called `\textit{serialInterfaceScripts}.' Within this directory are sub-directories containing scripts for controlling the stage via MATLAB, Python, or LabView. The MATLAB functions are the most mature and well tested. The Python and LabView stuff has been verified to work but so far not used beyond this. 

To get the MATLAB scripts working, add the directory which contains the files to your MATLAB path. Edit the \textit{connectOpenStage.m} file so that it points to the correct serial port. Save the file. The first time you run one of the commands in that directory it will automatically try to connect to the stage. Try running OS\_getInfo, which queries the stage for a bunch of useful information. You should see MATLAB attempt to form a connection with the stage then a bunch of information will appear on the screen. If this occurs, then you have a connection back and forth with the stage. If it doesn't, find out why. 

The rest of the functions should be fairly self-explanatory. OS\_getPosition returns the current position of each axis in microns. OS\_goto will move the stage, by default motions are to an absolute position but it also does relative positions. See its help docs. OS\_beep works the speaker. OS\_zero will zero the LCD counters. Calling some functions, such as OS\_stepSize with no input arguments will cause the stage to report the current step size. Add the appropriate input argument and a new step size is set. \textbf{NOTE: do not use full steps! See below for why.}

\subsection{Accuracy}
The stage should have relative accuracy of well under a micron. i.e. you should be able to make many motions in different directions then return to zero and be in virtually the same position give or take half a micron or so. If this isn't happening then likely you have an issue with the motors skipping. It would be wise to take the time to read our paper, as it describes in detail the steps you can take to get high accuracy motions. The information in the paper is summarized below. 

The stage controller has no feedback. It issues motion commands as TTL step pulses and the motors make small steps of a known size each time a pulse is received. If the motors fail to step, the OpenStage controller won't know and you'll get under-shoots. Under normal use conditions, the motors are \textit{very reliable} and skipped steps are not an issue. We have run our system for months and had no problem with this. The motors will step virtually 100\% of the time when told to do so. If they are failing to step then something is wrong. The main cause of skipped steps is lack of torque: you're asking the motors to move a load they cannot push. If this happens they'll skip steps and usually this skipping is very obvious (often a grating noise occurs). 

In a stepper motor, torque decreases with increasing speed. So moving too fast will cause skipped steps. The higher the load on the motors, the lower the maximum speed. If you accelerate too quickly the motors may skip. If the current is too low, the motors will skip. If you're using full steps, it's very likely you will get many skipped steps unless the motor current is set \textit{just right}. So avoid full steps. Half steps and smaller are much smoother and won't skip. If you don't know anything about stepper motor microstepping, then do a little Googling or read our paper.

\subsection{Stage Speed}
The main limitation of the current firmware is the way in which it handles pulse rates. The accelstepper library, which is used to issue the step pulse pulses and implement acceleration and deceleration, has some substantial limitations. If speed is a concern, read the following carefully. 

Firstly, the OpenStage firmware can issue a maximum step pulse rate of about 4~kHz in one axis. So to get the fastest motions you will have to move in half steps. Avoid full steps if possible. Full steps can work, but the current to the motors has to be just right or they will skip. If you want to move fast, use a 500~$\mu m/rev$ micrometer. As you can see, there is a trade off between speed and accuracy. 

Secondly, this maximum speed drops when multiple axes are being moved together. For instance, if you command a motion of 5000~$\mu m$ in $z$ and 2000~$\mu m$ in $x$ then $z$ will move slowly until $x$ has reached its target position. 

Thirdly, OpenStage doesn't check that your requested maximum speed is even possible. So if you ask for, say, 2000~$\mu m/s$ with a 250~$\mu m/rev$ gear at half steps then you'd need well in excess of 4~$kHz$ to achieve this. OpenStage will simply move as fast as it can to reach the desired location; it will get there accurately but not at the speed you asked for. 

How can you explore the speed of your stage? To begin with, hook up the BNC connection of the axis of interest to a scope. You'll be able to see the frequency of the pulse trains going to the motor. In addition, issue the 
\textit{OS\_getInfo} command. This will show you the target pulse rate for the speed and step size you've chosen. Likely you will find it's undershooting the desired pulse rate. 

Can the firmware be improved? The accelstepper library appears to generate the timing pulses using software. However, the Arduino Mega has three spare hardware timers. There is currently a (very) beta version of the firmware that uses these hardware timers to produce the pulse trains. The advantages of this are that we can generate much higher frequency pulse trains (about 25~$kHz$) and this can be done using multiple axes simultaneously with no speed loss. This will allow for higher speed accuracy. If you're interested in this, please e-mail me to speed up development. It may be some time before I have a working version of this firmware. 

\end{document}

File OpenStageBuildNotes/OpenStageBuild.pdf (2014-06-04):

## Introduction

These are the instructions for building the OpenStage microscope stage controller based around a Rev 2 PCB. The Rev2 board is a prototype and contains some mistakes that you will have to work around. None of these mistakes are show-stoppers, they just result in some cosmetic kludges. Read the whole way through this guide before you start soldering. Think before you solder: you are the first (or one of the first) to build this thing so there may be mistakes in the guide. Please report your experience and any errors you find. Some steps have various solutions: choose the one that works best for you. The Rev 2 board has the following issues, all of which have solutions¹
:
Issue | Solution
LCD header is inverted | Connect LCD to PCB via a ribbon cable, to flip the lines left/right
Serial comms socket is inverted | snip off socket pins 1 and 4. Solder socket into place. Connect solder pads at positions 1 and 5 and also at positions 2 and 4.
Power switch drill holes too small | Drill out (carefully!)
Top left LCD spacer drill hole too close to jumper | Either don’t use this spacer or short jumper using sol-der or wire, this will provide enough room to screw in a spacer.
Some drill holes for case mount-ing overlap with mounted com-ponents | User other drill holes–there are loads.
Motor serial connectors are a lit-tle closer to each other | Serial sockets that plug into the connectors do fit side by side (just!)
Connections from Quadstepper motor outputs to Openstage PCB are a bit crap. | I’m looking for suggestions!

1Your board will likely come with the power switch holes drilled out and a serial port connector correctly wired

Figure 1 shows the bare PCB, as it looks like before you start. Figure 2 shows roughly what the board will look like when it’s finished, with the components installed. Optional buttons near the top of the front of the board haven’t been installed here. The LCD display will not just slot into the header, unfortunately, as the connections are backwards. You should probably solder the wiring for the LCD display right at the end.


Figure 1: Front (left) and back (right) views of the bare PCB.


Figure 2: Front (left) and back (right) views of the finished PCB.

## Getting power to your board

The first thing we’ll do is hook up the components related to powering the board. You’ll install the main power switch, input jack, the 9V regulator which powers the Arduino and USB host shield, and the MOSFET that is used for reverse current protection.
Install the power switch (Fig. 3) so it’s facing frontwards (i.e. the solder will be applied to the back of the board). In Rev 2 boards the drill holes are too small for this switch and they’ve been expanded to allow the switch to fit. Solder will not take on the lower, unused, switch connection. This is not a problem. Next solder the power jack, MOSFET, and 20k resistor to the back of the board (Fig 3). The MOSFET and resistor are surface mount, so all the soldering is to the back face of the board. The power jack is through hole, so it’s inserted into the back face and you solder to the front face.

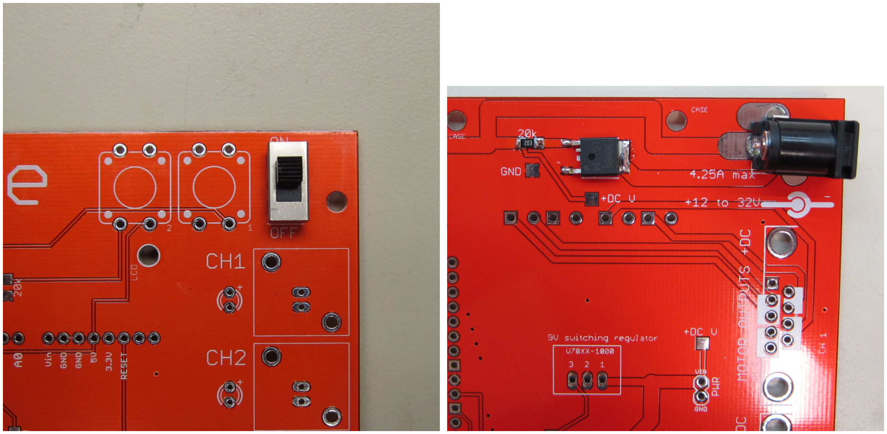
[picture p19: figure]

Figure 3: Power switch (left). Power jack and reverse polarity protection (right).

## Soldering small surface mount components

Soldering the surface mount resistors is not too tricky once you have the technique down. First apply a little solder to one pad (Fig. 4) then solder resitor to this pad with the aid of forceps (Fig. 5). Finally, solder the remaining pad (not shown).


Figure 4: Solder applied to one pad in preparation for soldering a resistor in place. Image shows two pairs of reistor pads. Solder has been applied to the upper pad of each pair.


Figure 5: Rest resistor on one pad. Keep in place with forceps. Apply solder.

Solder the two surface-mount capacitors to the front of the board (Fig. 6, left). The capacitor with the higher voltage rating goes on the input side of the regulator (the lower pair of pads, nearer the serial ports). Then solder into place the 9V regulator to the rear of the board (Fig. 6, left). The regulator has a dot indicating which pin is number 1.

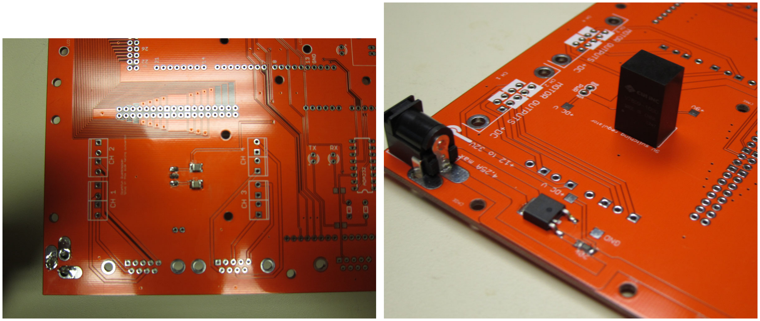
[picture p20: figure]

Figure 6: Capacitors for 9V regulator (left). 9V regulator (right).

## Testing the power

At this point you have enough circuitry on-board to check that the power is being distributed correctly. Apply the probe leads across to points which ought to be supplying the full input voltage. The inputs to the QuadStepper are a good place (Fig. 7, left). In the example images, we’re using a 24V supply. We measure 24V when we do this. This should be under the control of the board’s power switch. Next check that you get 9V after the regulator. You can use the 9V test pad and any ground connection (including the Quadstepper’s ground you previously used to measure the full input voltage). This should read close to 9V (Fig. 7, right). Finally, you can switch the polarity of the input jack if you wish. You should no longer be able to pick up a voltage. This indicates that the MOSFET-based reverse polarity protection is working as expected.

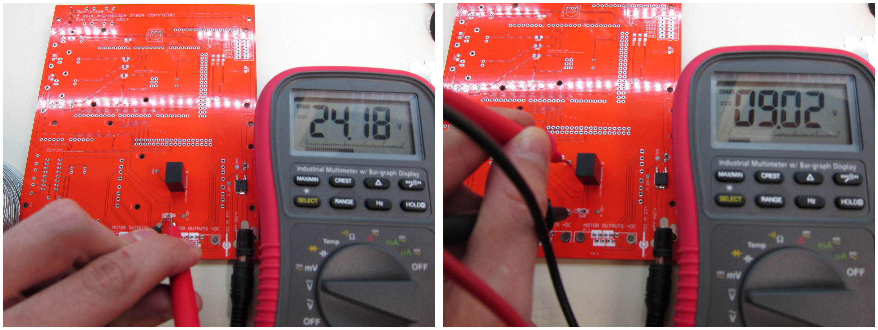
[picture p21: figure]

Figure 7: Measuring input voltage (left), in this case 24V. Measuring output of 9V regulator (right).

## Attach small components

Now is a good time to solder into place the smaller components. There are 15 resistors to attach. Six of these are current-limiting resistors for the indicator LEDs. If you want the LEDs bright then use a resistance of about 300Ω. If you want them dim, then about 2500Ω to 3000Ω should do the trick. The remaining 9 resistors are current limiting resistors for the debugging lines; these are all 300Ω. The buzzer is attached to the front face of the board. The ADM232 (Fig. 8) IC and associated capacitors attach to the front face of the board. Also shown in Fig. 8 are the two indicator LEDs. These may have little ‘shoulders’ on the pins that will prevent the LEDs from being fully inserted. If this is the case, you can clip away the shoulders. Insert the remaining 4 indicator LEDs. Attach the 5kΩ trim pot to the back of the board (Fig. 9). Optionally, attach the Wago terminal connector for the debugging lines (Fig. 9).


Figure 8: ADM232 serial comms IC and associated capacitors.

## Soldering the headers for the Arduino and USB host shield

This is the most tedious bit but it’s also the easiest to get wrong. Make sure the headers go into the correct side of the board. Let’s start with the Arduino Mega male headers (Fig. 9). These should be on the back face of the board. The idea is to have the Mega facing inwards on the back face, as shown in Fig. 9. You will likely have to cut the single male rows from a longer strip. Once you’re done here, do the headers for the USB host shield (Fig. 10). This also attaches to the back face of the OpenStage PCB. In this case we’ve soldered female headers to the OpenStage board and male headers to the USB host shield. It work equally well the other way around.


Figure 9: Shows Arduino Mega headers, trim pot, and Wago terminal block. Note that the middle 2x3 header for the Mega is female.


Figure 10: USB host shield shown with headers attached.

## Hooking up the Quadstepper

Connecting the Quadstepper is a little more involved. First of all, you’ll need to remove its power input jack. This is surface mount so you easily can snip off at the four attachment points. Do this carefully so you don’t rip up any traces: one of the solder pads is part of a trace. If you do damage it, you’ll have to bridge the gap with wire. This done, solder male headers to the underside of the newly-revealed 1x2 DC power connectors. Then attach male headers to the 2x19 strips. These are the digital control inputs for the motors. Again, these go on the underside of the Quadstepper, so you can mount it facing outwards on the front of the OpenStage PCB (Fig. 2). Then solder the corresponding female adapters to the front of the OpenStage PCB.
The final step, the motor outputs, is a bit of an adventure. The pitch of these header holes is 0.15” and strip headers aren’t available with this spacing. I’ve yet find a neat solution, so I present two options here. One, which allows you to easily remove the Quadstepper, is to attach male single pins to each motor output on the Quadstepper then cut 1x3 female adapters down to 1 pin and attach these to the OpenStage PCB. This looks like crap (Fig. 11, left), and you may need a glue gun get the female headers sitting properly before you solder them. Thus, an alternative is to solder the motor connections with short wires (Fig. 11, right). This looks nicer, but it means you can’t get the Quadstepper off very easily. Given that there is no reason to remove it, the latter option might be the easier. Once you’ve done this, solder into place the two female DB9 sockets for the motor outputs.

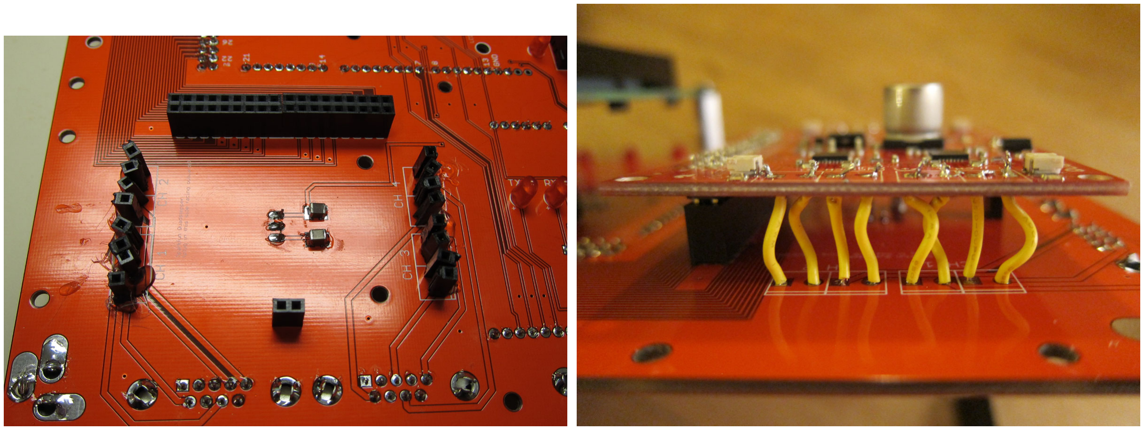
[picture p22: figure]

Figure 11: Quadstepper female headers on OpenStage PCB (left) or using wires (right)

## Wiring up the LCD display

Because this a Rev 2 board, the LCD display won’t just slot into place with a male and female header. This is because the connection on the board is inverted. To get around this, the easiest thing is to use a ribbon cable to invert inputs. You want to have something that looks like Figure 12. There are a bunch of ways you could do that. In the images shown, I’ve soldered a male strip header to the back of the LCD display. The 16 wire ribbon is soldered directly onto those pins. The other side of the cable has a female header on it. This female header connects to a 90 degree male header on the back of the OpenStage board. You could equally well solder directly the LCD. See how much space you have and what works best for you. If you wish to attach the BNC connectors next to the LEDs, you could do this now. These BNC connectors allow you to monitor the step pulse trains going to the motors.

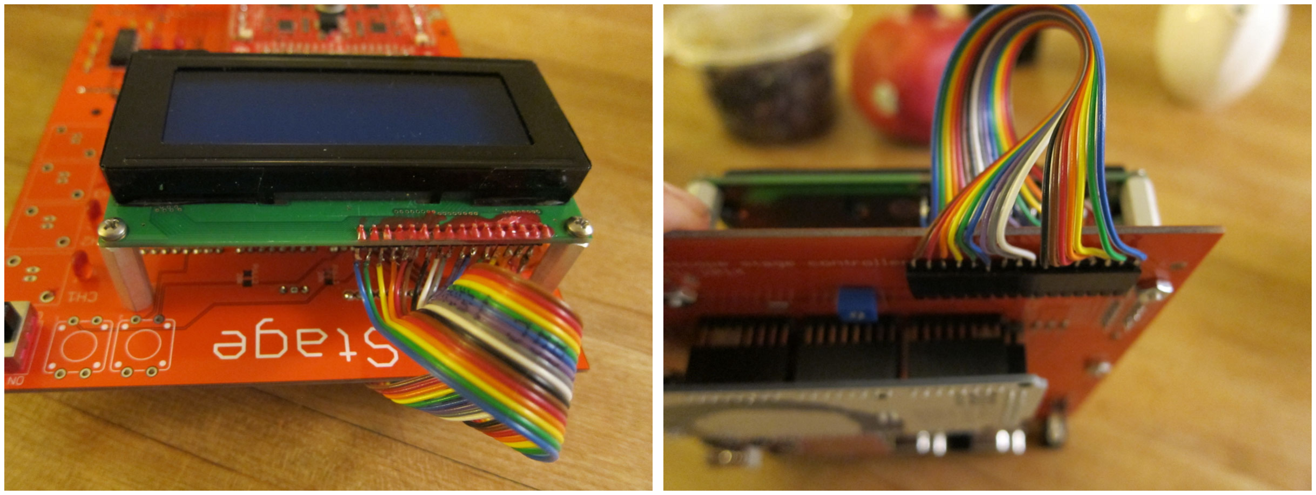
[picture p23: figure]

Figure 12: Using a ribbon cable to invert the LCD inputs.

## Connecting the motors to the DB9 cables

Get a M/M DB9 cable and cut in half. Strip and expose the leads. You will be using 4 or 6 wire stepper motors. 6 wire steppers will have one pair of wires that aren’t connected to anything. Stepper have two sets of coils inside and each set of coils is connected to one pair of wires. Use your datasheet or a continuity tester to figure out which wires form a pair. If you have 6 wire steppers, you will need the datasheet to make sure you avoid using the middle wires from each coil. Each row on the female DB9 connectors is for one motor. On the bottom row, pins 6&7 connect to one coil and 8&9 connect to the other coil. On the top row, pins 5&4 form a pair and pins 3&2 form a pair. Pin 1 is unused. It doesn’t matter which coil connects to which pair of pins, but switching the coils will switch the default motor direction²

## Uploading the firmware

The board should now be assembled. Plug in the Arduino Mega, USB host shield, and Quadstepper. If it’s not already programmed, hook up the Mega to a PC and upload the OpenStage firmare from the Github page (https://github.com/raacampbell13/openstage). You can download as a zip (easy) or clone the repository (if that’s your thing). You will also need to download and install the Arduino USB Host Shield library (<https://github.com/felis/USB_Host_Shield_2.0>) and the AccelStepper library (<http://www.airspayce.com/mikem/arduino/AccelStepper/>).
If you haven’t programmed an Arduino before, here’s what you’ll need to do. Download the Arduino IDE from arduino.cc. Install the IDE. The source code for the OpenStage firmware
is in the ‘OpenStage’ sub-directory from the Github repository. There are a bunch of source code files here. Unless you want to make significant changes to the firmware, you don’t need to be concerned with most of this. All you care about is the user settings file. There are a bunch of different potential user settings files, depending on the desired configuration of the stage. We want the c userSettings MEGA PCB file. This file should have the extension ‘.ino’; if it has ‘.BAK’, or any other extension, then rename the file. It should be called ‘’c userSettings MEGA PCB.ino’. When you try to compile the firmware, the Arduino IDE simply concatenates the .ino files in the directory then compiles the resulting, larger, file. You don’t want it to include any of the other c userSettings* files. So either delete them or make sure none of them end in .ino
Now you’re good to go! Open the file ‘OpenStage.ino’ in the Arduino IDE. When you do this, a new window will pop up and it will have about a dozen tabs. Each is a source file (.ino file) from the directory. Go to the tab called c userSettings MEGA PCB. If that tab doesn’t exist, you didn’t rename the file correctly. If there are any other tabs starting with ‘c ’ then you didn’t remove or rename the extra settings files. If you have such issues, close the IDE and rename files to fix the problem. In the c userSettings MEGA PCB tab you can modify the user settings for your rig. You will want the LCD display and, presumably, the game pad, so don’t alter the first three lines. If you want to communicate with the stage via the Arduino USB port, not a regular serial port, then change the value of controlViaUSB to 1.

2There will soon be a way of switching default motor direction in the user settings section of the source code firmware. Currently, the only way is to switch the wiring.

You will need to carefully set the ‘Microscope axis hardware definitions.’ If you want three axes then leave the first bit of that section (up to ‘gear ratio’) as is. What you likely will need to do is modify the gearRatio vector. Those numbers indicate the number of microns the stage will advance when the micrometer rotates revolution. e.g. The standard ThorLabs micrometers are 100 turns per inch; the imperial units advance 635 µm per revolution and the metric ones 500 µm per revolution. Each axis can have a different value, allowing finer motions for z, say. Similarly, you will need to define the number of degrees the stepper motors advance when they take a full step. Chances are you will have motors which are 1.8 degree (200 steps per revolution) or 0.9 degree (400 steps per revolution). Armed with these two pieces of information, OpenStage can determine its relative position in space with very high accuracy.
The remaining parameters are less critical. They relate to things such as the speeds and step sizes that the PS3 game pad produces and the default speeds on each axis for PC-based control. Many of these settings can be altered via the serial port (see the serial port commands directory). You won’t need to change the pin definitions at the end of the file.

## Powering up!

You’re now ready to power up. Connect your power line and PS3 game pad. Hook up the motors (do not plug or unplug the motors with the power on). If you want computer control, hook up the USB cord or the serial port to your PC. To begin with, it might be sensible not to connect the motors to the rig. Attach little pieces of tape to the spindle to watch them move. Make sure the switch on USB host shield is set to ‘on’. Switch on OpenStage. You should see a ‘Booting...’ message on the LCD display. The boot sequence should complete in about 5 seconds. Once it has booted you can control the stage using either a PC or the gamepad.
The Quadstepper has 4 potentiometers, one for each motor. These control how much current is delivered to the coils. The power supply determines the voltage to the coils. If the current is too high the motors and the driver chips can run very hot. It shouldn’t be necessary to run at high currents. Choose a low current at work your way up. You shouldn’t need a heatsink on the motor. You might like to add a heatsink to the driver chips; again, however, this likely isn’t necessary as they should be running cool. If the current is too low the motors will skip (see below).

Control via gamepad

The PS3 gamepad serves as a comfortable input device. The LCD displays current speed and position of each axis. The display is updated regularly, except at the fastest speed mode (see below) where it updates only at the conclusion of motion. The PS3 DualShock controller provides the following functionality:

- Analog control of speed and direction for each axis is provided by the two analog sticks. The left stick controls X and Y and the right stick controls Z, and the 4th axis (z) if this is enabled. Larger stick displacements are mapped to higher motion speeds, making it easy to manually guide the stage at exactly the desired speed.

- Fixed-size motion steps are provided by the direction pad (D-pad). For instance, pressing the left D-pad button moves the stage one increment to the left. By default the D-pad controls X/Y motions; holding down the Triangle button whilst pressing up or down on the D-pad yields fixed step size motions in Z, with Triangle plus L/R yielding motions in z.
- The two shoulder buttons (L1 and R1) allow the user to cycle between 4 different Speed Modes. The selected speed mode influences both the maximum speed of analog stick motions and the size of the D-pad motion steps. Speed mode #1 provides a nominal maximum speed of 3 µm/s, #2 is 25 µm/s, #3 is 100 µm/s, and #4 is 750 µm/s. The size of the D-pad steps range from 3 µm to 50 µm. Changing the speeds and motion steps sizes involves only trivial modifications to the source code (see above). The currently selected Speed Mode is indicated by the 4 LEDs on the DualShock. The stage boots in a low speed mode for safety reasons.
- The user can store up to 4 locations and return to them later using the 4 right-hand buttons. Firmly press on a button for 1 second to store the current stage position. The controller produces an audible indication when a new location is stored. Return at any time to the stored location by double-clicking on the corresponding button. OpenStage returns to the stored position at maximum speed, as defined in the settings file.

Control via PC

The Github repository contains a directory called ‘serialInterfaceScripts.’ Within this directory are sub-directories containing scripts for controlling the stage via MATLAB, Python, or LabView. The MATLAB functions are the most mature and well tested. The Python and LabView stuff has been verified to work but so far not used beyond this.
To get the MATLAB scripts working, add the directory which contains the files to your MATLAB path. Edit the connectOpenStage.m file so that it points to the correct serial port. Save the file. The first time you run one of the commands in that directory it will automatically try to connect to the stage. Try running OS getInfo, which queries the stage for a bunch of useful information. You should see MATLAB attempt to form a connection with the stage then a bunch of information will appear on the screen. If this occurs, then you have a connection back and forth with the stage. If it doesn’t, find out why.
The rest of the functions should be fairly self-explanatory. OS getPosition returns the current position of each axis in microns. OS goto will move the stage, by default motions are to an absolute position but it also does relative positions. See its help docs. OS beep works the speaker. OS zero will zero the LCD counters. Calling some functions, such as OS stepSize with no input arguments will cause the stage to report the current step size. Add the appropriate input argument and a new step size is set. NOTE: do not use full steps! See below for why.

Accuracy

The stage should have relative accuracy of well under a micron. i.e. you should be able to make many motions in different directions then return to zero and be in virtually the same position give or take half a micron or so. If this isn’t happening then likely you have an issue with the motors skipping. It would be wise to take the time to read our paper, as it describes in detail the steps you can take to get high accuracy motions. The information in the paper is summarized below.
The stage controller has no feedback. It issues motion commands as TTL step pulses and the motors make small steps of a known size each time a pulse is received. If the motors fail to step, the OpenStage controller won’t know and you’ll get under-shoots. Under normal use conditions, the motors are very reliable and skipped steps are not an issue. We have run our system for months and had no problem with this. The motors will step virtually 100% of the time when told to do so. If they are failing to step then something is wrong. The main cause of skipped steps is lack of torque: you’re asking the motors to move a load they cannot push. If this happens they’ll skip steps and usually this skipping is very obvious (often a grating noise occurs).
In a stepper motor, torque decreases with increasing speed. So moving too fast will cause skipped steps. The higher the load on the motors, the lower the maximum speed. If you accelerate too quickly the motors may skip. If the current is too low, the motors will skip. If you’re using full steps, it’s very likely you will get many skipped steps unless the motor current is set just right. So avoid full steps. Half steps and smaller are much smoother and won’t skip. If you don’t know anything about stepper motor microstepping, then do a little Googling or read our paper.

Stage Speed

The main limitation of the current firmware is the way in which it handles pulse rates. The accelstepper library, which is used to issue the step pulse pulses and implement acceleration and deceleration, has some substantial limitations. If speed is a concern, read the following carefully.
Firstly, the OpenStage firmware can issue a maximum step pulse rate of about 4 kHz in one axis. So to get the fastest motions you will have to move in half steps. Avoid full steps if possible. Full steps can work, but the current to the motors has to be just right or they will skip. If you want to move fast, use a 500 µm/rev micrometer. As you can see, there is a trade off between speed and accuracy.
Secondly, this maximum speed drops when multiple axes are being moved together. For instance, if you command a motion of 5000 µm in z and 2000 µm in x then z will move slowly until x has reached its target position.
Thirdly, OpenStage doesn’t check that your requested maximum speed is even possible. So if you ask for, say, 2000 µm/s with a 250 µm/rev gear at half steps then you’d need well in excess of 4 kHz to achieve this. OpenStage will simply move as fast as it can to reach the desired location; it will get there accurately but not at the speed you asked for.
How can you explore the speed of your stage? To begin with, hook up the BNC connection of the axis of interest to a scope. You’ll be able to see the frequency of the pulse trains going to the motor. In addition, issue the OS getInfo command. This will show you the target pulse rate for the speed and step size you’ve chosen. Likely you will find it’s undershooting the desired pulse rate.
Can the firmware be improved? The accelstepper library appears to generate the timing pulses using software. However, the Arduino Mega has three spare hardware timers. There is currently a (very) beta version of the firmware that uses these hardware timers to produce the pulse trains. The advantages of this are that we can generate much higher frequency pulse trains (about 25 kHz) and this can be done using multiple axes simultaneously with no speed loss. This will allow for higher speed accuracy. If you’re interested in this, please e-mail me to speed up development. It may be some time before I have a working version of this firmware.

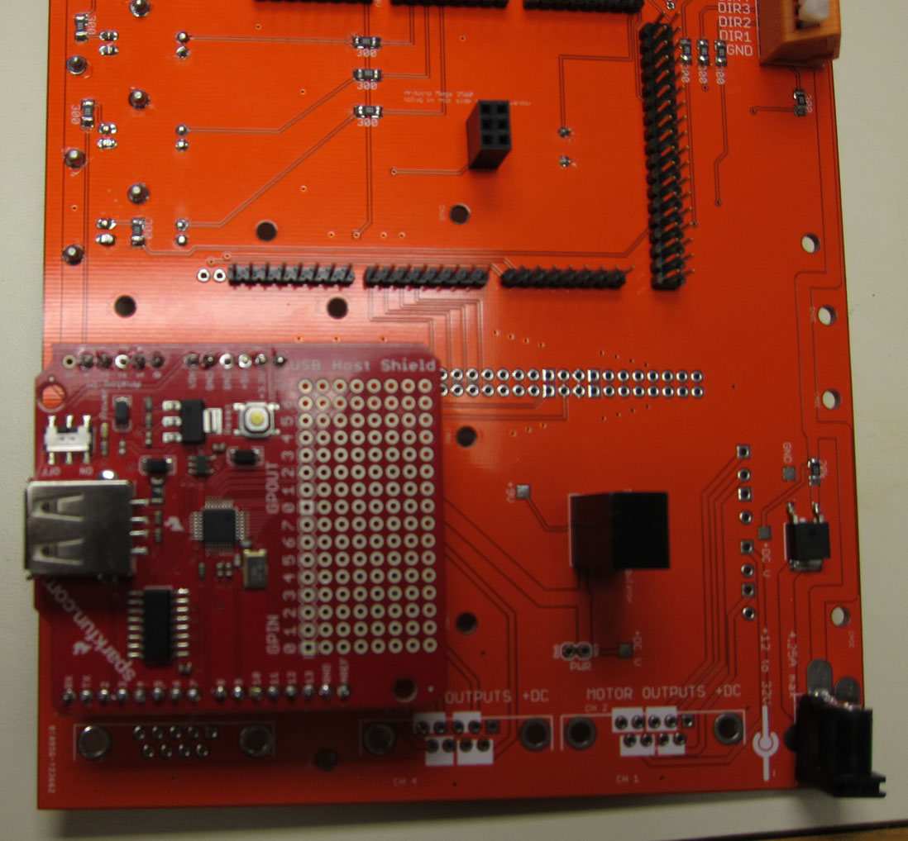
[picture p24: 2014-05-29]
OpenStageBuildNotes/images/IMG_3210.JPG

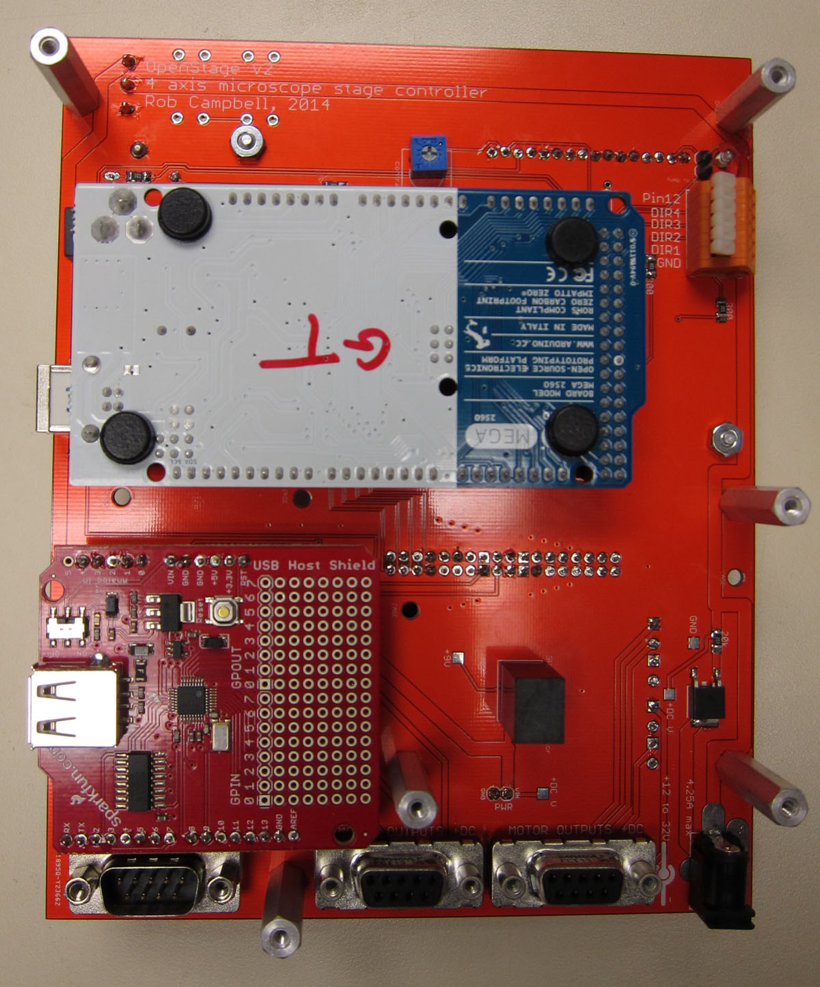
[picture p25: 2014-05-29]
OpenStageBuildNotes/images/IMG_3214.JPG

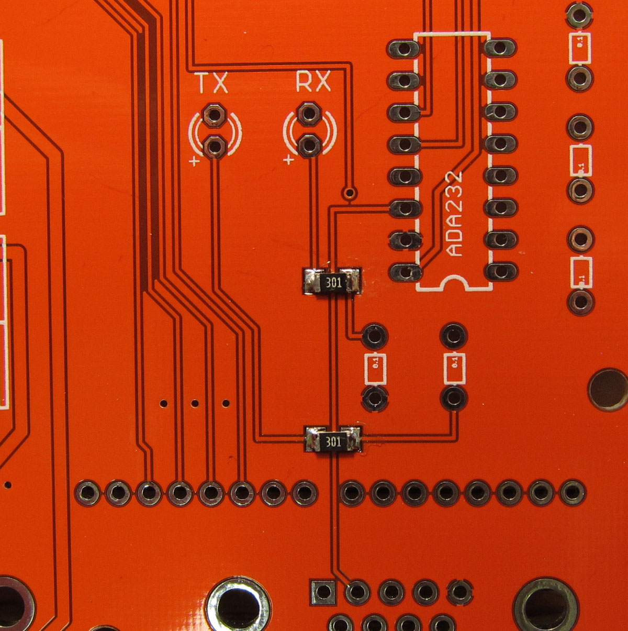
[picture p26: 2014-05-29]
OpenStageBuildNotes/images/IMG_3199.JPG

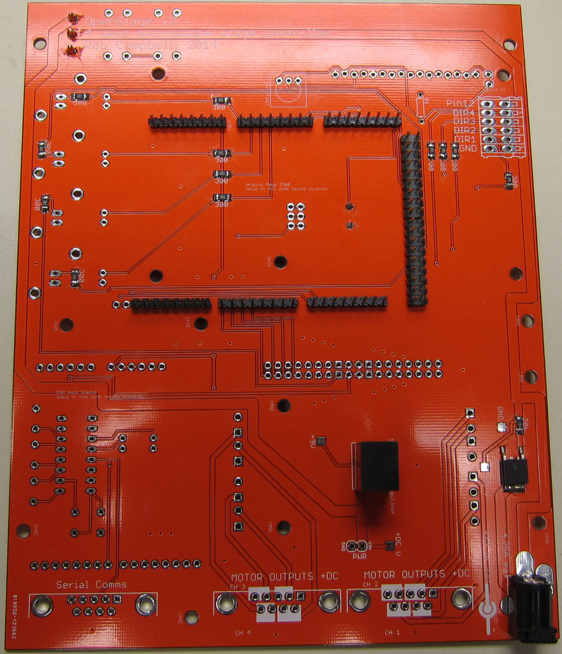
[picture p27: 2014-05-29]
OpenStageBuildNotes/images/IMG_3202.JPG

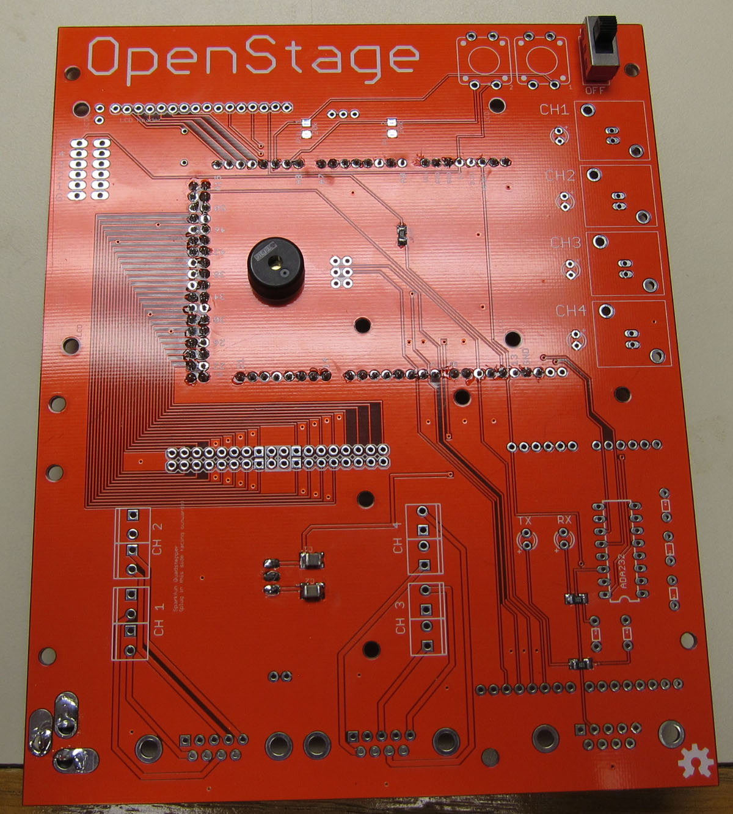
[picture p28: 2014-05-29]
OpenStageBuildNotes/images/IMG_3201.JPG

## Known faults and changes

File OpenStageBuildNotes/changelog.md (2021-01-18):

# Changes since initial release

## 2021-14-18

The Sparkfun quad stepper board has been discontinued, so in this revision it has been replaced with four "Step Stick" (aka Pololu Carrier) drivers. These are available from various sources with a range of driver ICs, such as the cheap [A4988](https://www.pololu.com/product/1182), more efficient [DR8825](https://www.pololu.com/product/2133) or the quiet-running [TMC2100](https://uk.farnell.com/trinamic/tmc-silentstepstick/stepper-driver-board-2-phase-motor/dp/2822153) (silent step stick). The pinout of these modules are the same.

At the same time the connectors for the motors have been changed from DB-9 (two per motor) to M8 circular connectors (one per motor). The PCB/panel mount connector is the female [Amphenol M8S-04PFFR-SF8001](https://www.mouser.co.uk/ProductDetail/Amphenol-LTW/M8S-04PFFR-SF8001/) and the cable assembly is the male 
[8A-04AMMM-SL7A01](https://www.mouser.co.uk/ProductDetail/Amphenol-LTW/8A-04AMMM-SL7A01/). The genders of these can be swapped if desired, as the PCB footprint is the same for the male version of the Amphenol connector.

Extra capacitors are neeed for the stepper drivers. [100uF 16V radial, 5mm diameter, 2.5mm lead spacing](https://www.mouser.co.uk/ProductDetail/Panasonic/ECA-1CM101I/)

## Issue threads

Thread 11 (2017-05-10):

### ISSUE TITLE
Bluetooth lag

### ISSUE THREAD

**Issue by hughchurchill** [raacampbell/openstage#11]
First, let me say that openstage is awesome.  After frustrating SPI issues using Mega2560 + USB Host Shield, it was extremely easy to get it working after switching to a Mega ADK.

Using a PS4 gamepad via USB works very well, and while I can control the stage via bluetooth, there is significant lag (about 1 second).  I'm wondering if other users have experienced this and whether there is a known solution?

Using the same hardware and running the USB Host Shield example PS4BT, hat positions are printed with no lag, so there must be something in the openstage code that is slowing things down.

Thanks!

**Comment by raacampbell** [comment]
I'm glad it's useful! I never got bluetooth working at all, so you're doing better than me there. I'll ask a colleague of mine who I think is using OpenStage whether he tried bluetooth. 

Did you try bluetooth with really stripped down example code to see whether the lag is still present?

**Comment by raacampbell** [comment]
Nope, he hasn't tried bluetooth.

**Comment by hughchurchill** [comment]
Yes, using really stripped down example code from the USB host shield library, the game pad is read via Bluetooth with no lag. 

I'll poke around in the open stage code and will post here if I figure anything out. 

Thanks again for this project and the quick reply!

**Comment by raacampbell** [comment]
How odd. Let me know what you find.

**Comment by hughchurchill** [comment]
In e_mainLoop, I dropped ncycles from 3000 to 100 and it's working great, no lag!

To get bluetooth working, the only trick is to buy the right dongle, and the list on the USB host shield site gets outdated very quickly.  I am using [this one](https://www.amazon.com/gp/product/B002AQSTXM/ref=oh_aui_detailpage_o05_s00?ie=UTF8&psc=1).

I have to upload OpenStage to Mega ADK with this code in c_userSettings the first time to pair (press and hold SHARE and PS buttons):

//Create wired connection to PS3 gamepad on USB host shield. If you were to attempt a wireless (bluetooth)
//connection you'd want to edit the following code.  
//#include <PS4USB.h> //these are included in a_includes
//#include <PS4BT.h>
#ifdef DO_GAMEPAD
 USB Usb;
// PS4USB PS4(&Usb);  //apparently some dongles need this, mine didn't
BTD Btd(&Usb);
PS4BT PS4(&Btd, PAIR);
#endif

and after that, change to this code, upload OpenStage to Mega ADK, press PS button when serial asks:

//Create wired connection to PS3 gamepad on USB host shield. If you were to attempt a wireless (bluetooth)
//connection you'd want to edit the following code.  
//#include <PS4USB.h>
//#include <PS4BT.h>
#ifdef DO_GAMEPAD
 USB Usb;
// PS4USB PS4(&Usb);  //apparently some dongles need this, mine didn't
BTD Btd(&Usb);
PS4BT PS4(&Btd);
#endif

**Comment by raacampbell** [comment]
Thanks. I've linked to this Issue from the README.

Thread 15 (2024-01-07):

### ISSUE TITLE
Is there a circuit drawing?

### ISSUE THREAD

**Issue by khoroshyy** [raacampbell/openstage#15]
Hi.
Is there a circuit drawing?
Best.
Petro.

**Comment by raacampbell** [comment]
There are PCB files here: https://github.com/raacampbell/openstage/tree/master/OpenStage_PCB
There should be sufficient information on the wiring in the manuscript. Others have built based on that with no additional input.

**Comment by khoroshyy** [comment]
Thanks for pointing out,
I somehow missed the csh file but opened it in Kicad.
Best.
Petro.

**Comment by raacampbell** [comment]
Note that what's on GitHub now is a modified design, since some of the original parts no longer are available. I have not built the new design and I don't have the capacity to do so. I can help with general queries, though. The whole thing works surprisingly well, so if you are motivated you should be able to get it working.

**Comment by khoroshyy** [comment]
Thanks.
I am planning to reassign pins to use this board:
https://www.laskakit.cz/arduino-cnc-shield-v3/
Hopefully, it will be possible.
Best.
Petro.

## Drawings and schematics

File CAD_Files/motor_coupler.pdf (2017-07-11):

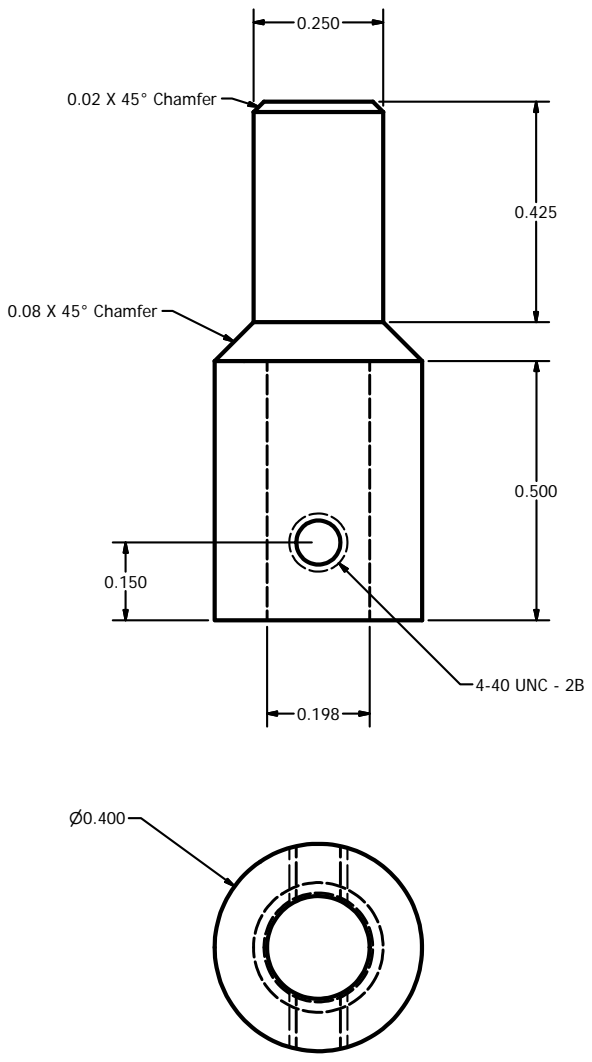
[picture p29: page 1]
TITLE; 0.02 X 45° Chamfer; 4-40 UNC - 2B; 0.08 X 45° Chamfer

DRAWN eifert | 10/21/2014

CHECKED

MFG

APPROVED

SIZE C | DWG NO motor coupler | REV

SCALE | | SHEET 1 OF 1

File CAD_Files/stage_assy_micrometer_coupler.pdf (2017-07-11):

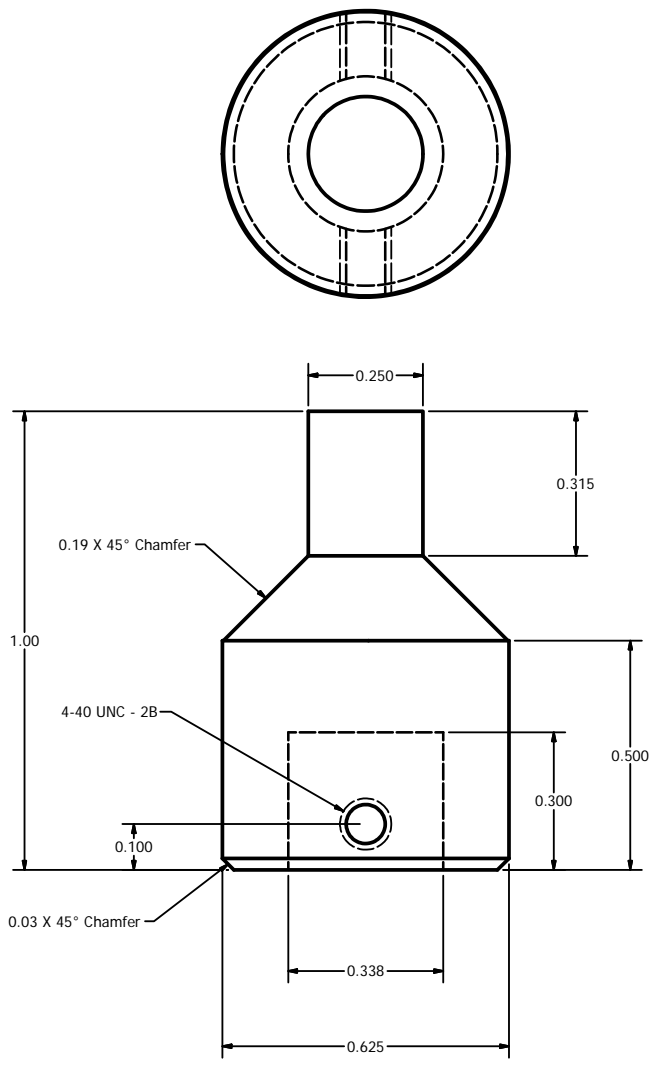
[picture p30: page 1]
TITLE; 0.03 X 45° Chamfer; 4-40 UNC - 2B; 0.19 X 45° Chamfer

DRAWN eifert | 10/21/2014

CHECKED

MFG

APPROVED

SIZE C | DWG NO stage assy micrometer coupler | REV

SCALE | | SHEET 1 OF 1

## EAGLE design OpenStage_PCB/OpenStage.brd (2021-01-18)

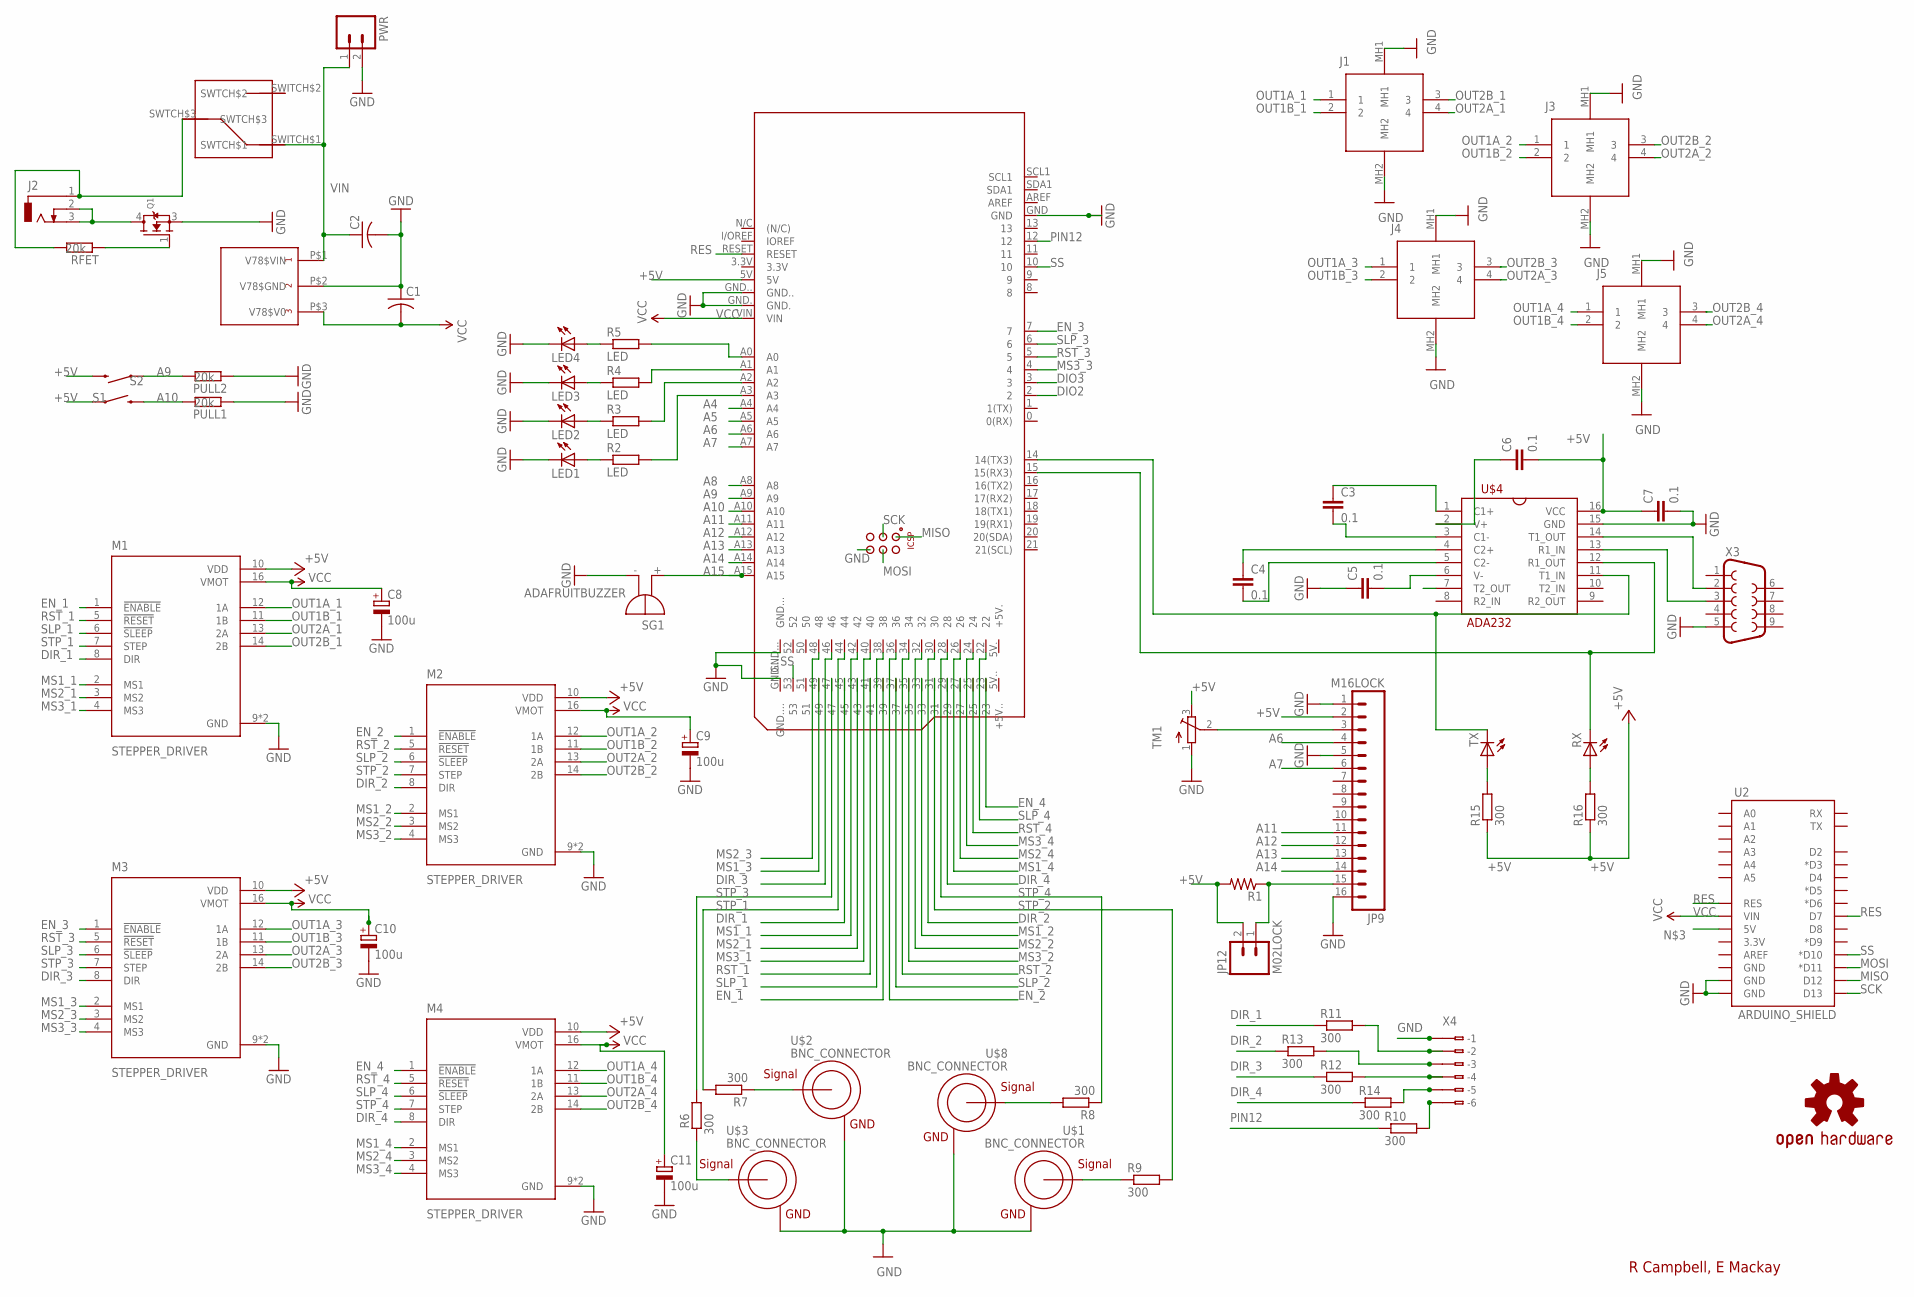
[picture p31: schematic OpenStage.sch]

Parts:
C1, C2: C-USC1210K; C1210K
C3, C4, C5, C6, C7: 0.1; AXIAL-5MM
C8, C9, C10, C11: 100u; E2,5-5
J1, J3, J4, J5: M8S-04PFFR-SF8001; M8S04PFFRSF8001
J2: DCJ0303
JP9: M16LOCK; 1X16_LOCK
JP12: M02LOCK; 1X02_LOCK
LED1, LED2, LED3, LED4: LED3MM
LOGO1: OSHW-LOGOL; OSHW-LOGO-L
M1, M2, M3, M4: STEPPER_DRIVER; POLOLU_CARRIER
PCB2: ARDUINO_MEGA_ROB
PULL1, PULL2: 20k; R3216
PWR: M02PTH; 1X02
Q1: MOSFET-N_TO252; TO252
R1: R-US_0204/7; 0204/7
R2, R3, R4, R5: LED; R3216
R6, R7, R8, R9, R10, R11, R12, R13, R14, R15, R16: 300; R3216
RFET: 20k; R3216
RX: LED3MM
S1, S2: SWITCH-MOMENTARY-212MM; TACTILE-PTH-12MM
SG1: ADAFRUITBUZZER; BMT1205XH7.5
TM1: TRIMPOT3386; TRIM-3386
TX: LED3MM
U2: ARDUINO_SHIELD; DUEMILANOVE_VIAS
U$1, U$2, U$3, U$8: BNC_CONNECTOR
U$4: ADA232; DIL16
U$5: V78XX-1000
U$6: SLIDING_SWITCH_0.185
X3: DB9FEMALE; DB9
X4: 233-206

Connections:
+5V: C6.P$2 (2), C7.P$1 (1), JP9.2, JP12.2, M1.10 (VDD), M2.10 (VDD), M3.10 (VDD), M4.10 (VDD), PCB2.5V, R1.2, R15.1, R16.1, S1.1, S2.3 (2), TM1.3 (E), U$4.16 (VCC)
A4: PCB2.A4
A5: PCB2.A5
A6: JP9.4, PCB2.A6
A7: JP9.6, PCB2.A7
A8: PCB2.A8
A9: PCB2.A9, PULL2.2, S2.1
A10: PCB2.A10, PULL1.2, S1.3 (2)
A11: JP9.11, PCB2.A11
A12: JP9.12, PCB2.A12
A13: JP9.13, PCB2.A13
A14: JP9.14, PCB2.A14
A15: PCB2.A15, SG1.+
DIO2: PCB2.2
DIO3: PCB2.3
DIR_1: M1.8 (DIR), PCB2.45, R11.1
DIR_2: M2.8 (DIR), PCB2.30, R13.1
DIR_3: M3.8 (DIR), PCB2.46, R12.1
DIR_4: M4.8 (DIR), PCB2.29, R14.1
EN_1: M1.1 (!ENABLE), PCB2.39
EN_2: M2.1 (!ENABLE), PCB2.36
EN_3: M3.1 (!ENABLE), PCB2.7
EN_4: M4.1 (!ENABLE), PCB2.23
GND: C1.1, C2.2, C5.P$1 (1), C7.P$2 (2), C8.-, C9.-, C10.-, C11.-, J1.MH1, J1.MH2, J3.MH1, J3.MH2, J4.MH1, J4.MH2, J5.MH1, J5.MH2, JP9.1, JP9.5, JP9.16, LED1.K (C), LED2.K (C), LED3.K (C), LED4.K (C), M1.9 (GND), M1.15 (GND), M2.9 (GND), M2.15 (GND), M3.9 (GND), M3.15 (GND), M4.9 (GND), M4.15 (GND), PCB2.GND, PCB2.GND., PCB2.GND.., PCB2.GND..., PCB2.GND...., PCB2.GND__, PULL1.1, PULL2.1, PWR.2, Q1.3 (S), SG1.-, TM1.1 (A), U2.GND@0 (GND), U2.GND@1 (GND), U$1.GND, U$2.GND, U$3.GND, U$4.15 (GND), U$5.P$2 (V78$GND), U$8.GND, X3.5, X4.B1 (B-1)
MISO: PCB2.MISO, U2.D12
MOSI: PCB2.MOSI, U2.D11 (*D11)
MS1_1: M1.2 (MS1), PCB2.42
MS1_2: M2.2 (MS1), PCB2.33
MS1_3: M3.2 (MS1), PCB2.49
MS1_4: M4.2 (MS1), PCB2.26
MS2_1: M1.3 (MS2), PCB2.43
MS2_2: M2.3 (MS2), PCB2.32
MS2_3: M3.3 (MS2), PCB2.48
MS2_4: M4.3 (MS2), PCB2.27
MS3_1: M1.4 (MS3), PCB2.40
MS3_2: M2.4 (MS3), PCB2.35
MS3_3: M3.4 (MS3), PCB2.4
MS3_4: M4.4 (MS3), PCB2.24
unnamed: R7.1, U$2.SIGNAL
unnamed: LED1.A, R2.1
unnamed: R9.1, U$1.SIGNAL
unnamed: LED2.A, R3.1
unnamed: LED3.A, R4.1
unnamed: LED4.A, R5.1
unnamed: PCB2.A0, R5.2
unnamed: PCB2.A1, R4.2
unnamed: PCB2.A2, R3.2
unnamed: PCB2.A3, R2.2
unnamed: JP9.15, JP12.1, R1.1
unnamed: PCB2.14 (14(TX3)), TX.K (C), U$4.11 (T1_IN)
unnamed: PCB2.15 (15(RX3)), RX.K (C), U$4.12 (R1_OUT)
unnamed: C3.P$1 (1), U$4.1 (C1+)
unnamed: C3.P$2 (2), U$4.3 (C1-)
unnamed: C4.P$1 (1), U$4.4 (C2+)
unnamed: C5.P$2 (2), U$4.6 (V-)
unnamed: C4.P$2 (2), U$4.5 (C2-)
unnamed: C6.P$1 (1), U$4.2 (V+)
unnamed: JP9.3, TM1.2 (S)
unnamed: U$4.13 (R1_IN), X3.3
unnamed: U$4.14 (T1_OUT), X3.2
unnamed: J2.1, RFET.2, U$6.SWTCH$3
unnamed: R8.2, U$8.SIGNAL
unnamed: R6.1, U$3.SIGNAL
unnamed: R11.2, X4.A2 (-2), X4.B2 (B-2)
unnamed: R12.2, X4.A4 (-4), X4.B4 (B-4)
unnamed: R13.2, X4.B3 (B-3)
unnamed: R14.2, X4.B5 (B-5)
unnamed: R10.2, X4.B6 (B-6)
unnamed: R15.2, TX.A
unnamed: R16.2, RX.A
unnamed: J2.2, J2.3, Q1.4 (D)
unnamed: Q1.1 (G), RFET.1
OUT1A_1: J1.1, M1.12 (1A)
OUT1A_2: J3.1, M2.12 (1A)
OUT1A_3: J4.1, M3.12 (1A)
OUT1A_4: J5.1, M4.12 (1A)
OUT1B_1: J1.2, M1.11 (1B)
OUT1B_2: J3.2, M2.11 (1B)
OUT1B_3: J4.2, M3.11 (1B)
OUT1B_4: J5.2, M4.11 (1B)
OUT2A_1: J1.4, M1.13 (2A)
OUT2A_2: J3.4, M2.13 (2A)
OUT2A_3: J4.4, M3.13 (2A)
OUT2A_4: J5.4, M4.13 (2A)
OUT2B_1: J1.3, M1.14 (2B)
OUT2B_2: J3.3, M2.14 (2B)
OUT2B_3: J4.3, M3.14 (2B)
OUT2B_4: J5.3, M4.14 (2B)
PIN12: PCB2.12, R10.1
RES: PCB2.RESET, U2.D7, U2.RES
RST_1: M1.5 (!RESET), PCB2.41
RST_2: M2.5 (!RESET), PCB2.34
RST_3: M3.5 (!RESET), PCB2.5
RST_4: M4.5 (!RESET), PCB2.25
SCK: PCB2.SCK, U2.D13
SLP_1: M1.6 (!SLEEP), PCB2.38
SLP_2: M2.6 (!SLEEP), PCB2.37
SLP_3: M3.6 (!SLEEP), PCB2.6
SLP_4: M4.6 (!SLEEP), PCB2.22
SS: PCB2.10, PCB2.53, U2.D10 (*D10)
STP_1: M1.7 (STEP), PCB2.44, R7.2
STP_2: M2.7 (STEP), PCB2.31, R9.2
STP_3: M3.7 (STEP), PCB2.47, R6.2
STP_4: M4.7 (STEP), PCB2.28, R8.1
VCC: C1.2, C8.+, C9.+, C10.+, C11.+, M1.16 (VMOT), M2.16 (VMOT), M3.16 (VMOT), M4.16 (VMOT), PCB2.VIN, U2.VIN, U$5.P$3 (V78$V0)
VIN: C2.1, PWR.1, U$5.P$1 (V78$VIN), U$6.SWITCH$1 (SWTCH$1)

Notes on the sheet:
R Campbell, E Mackay

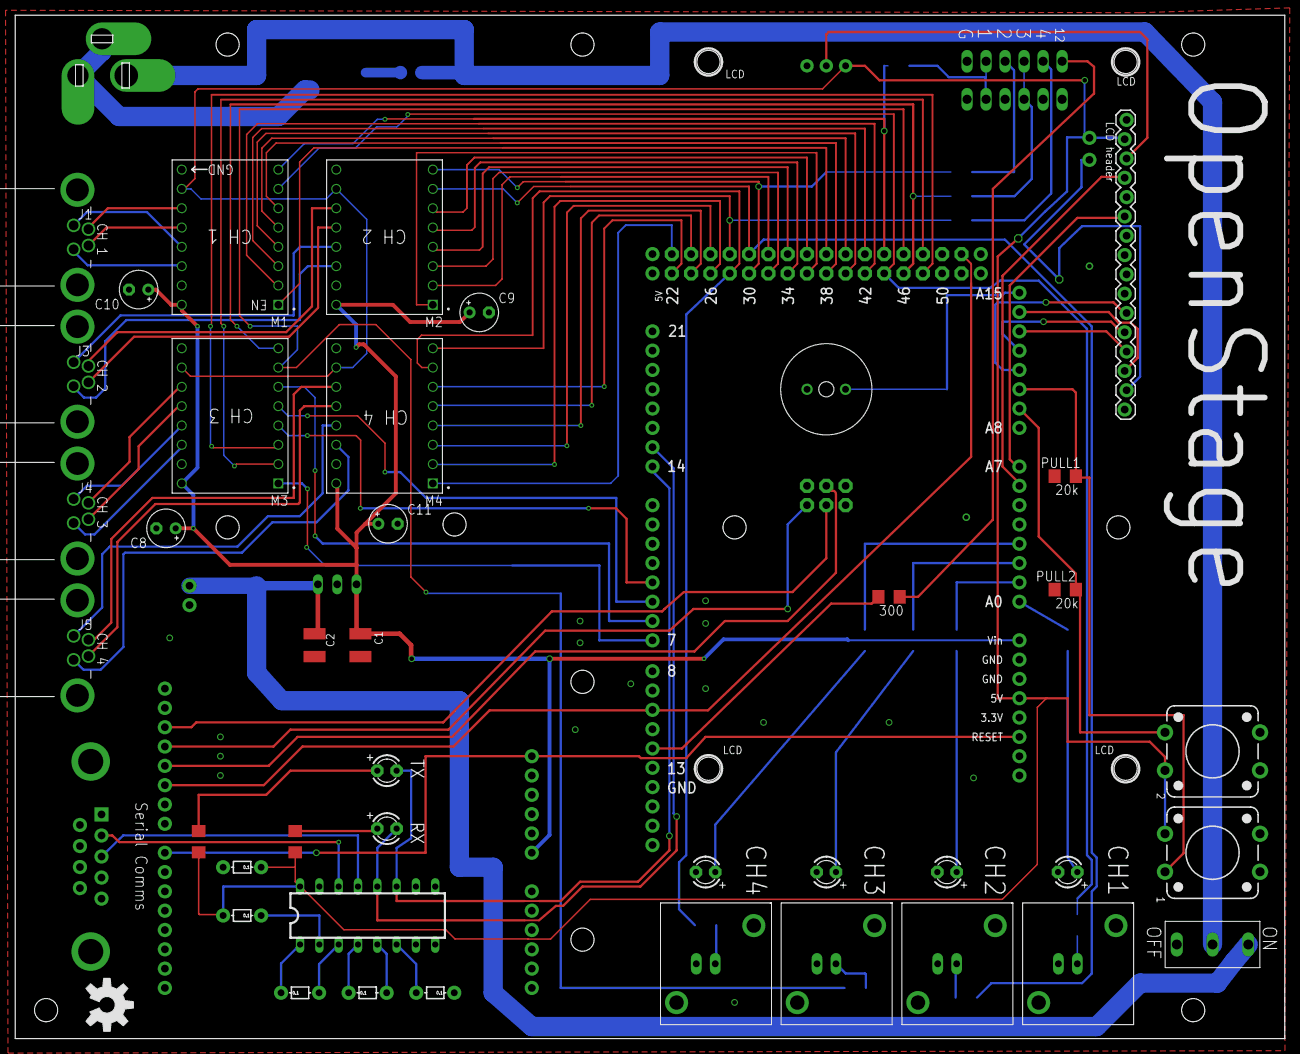
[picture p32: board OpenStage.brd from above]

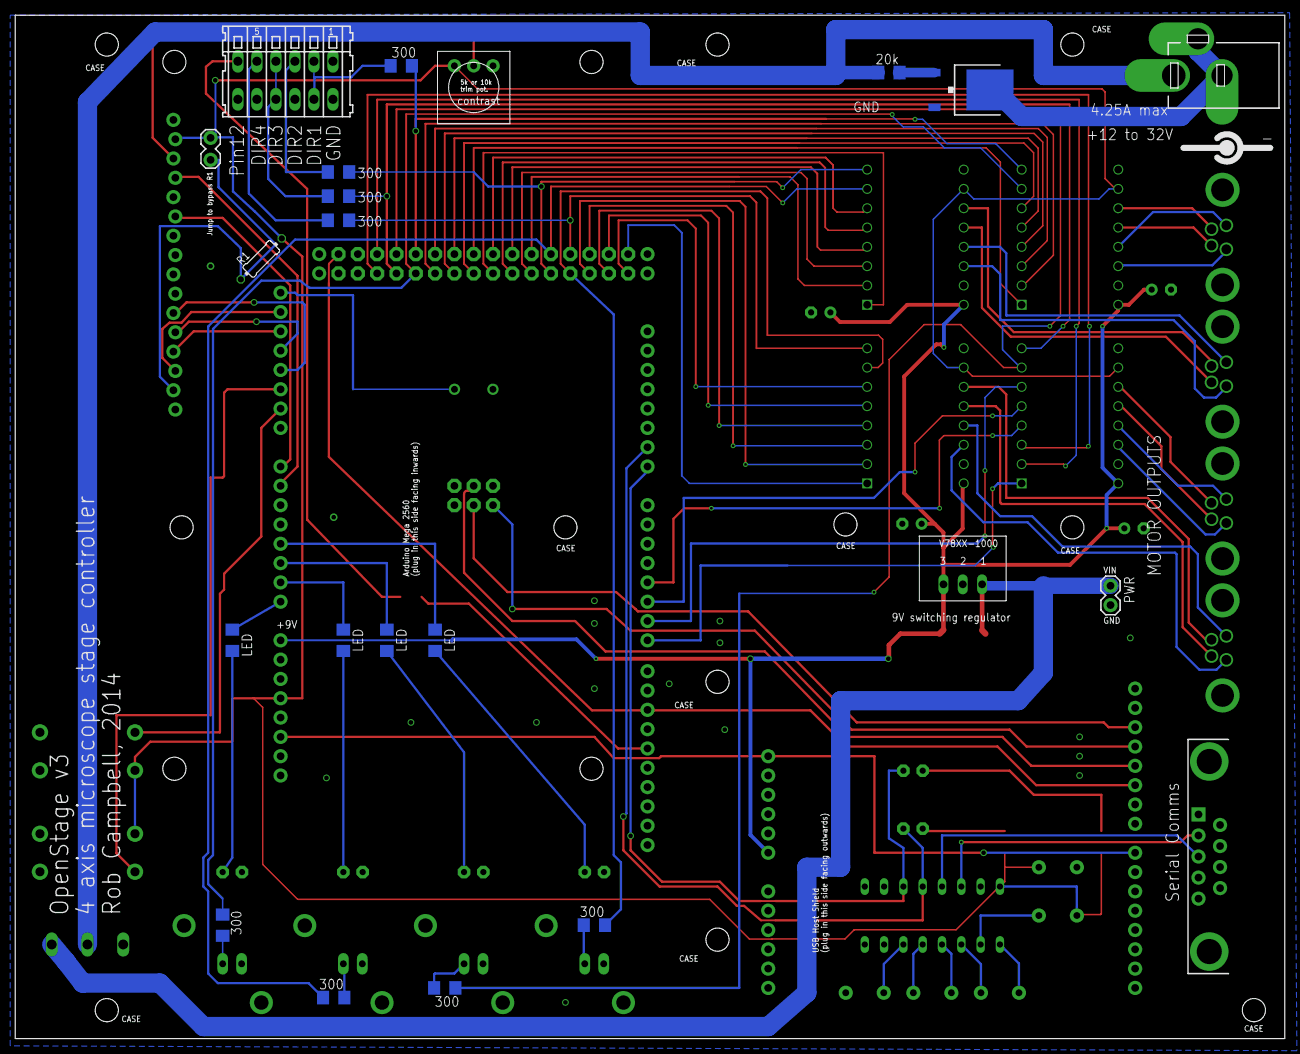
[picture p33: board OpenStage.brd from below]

Board: 2 copper layers, 167.0 x 134.6 mm, 65 parts (23 on the bottom side), 101 nets.

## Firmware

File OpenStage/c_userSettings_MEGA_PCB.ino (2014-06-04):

// Some global definitions that need to be modified by the user for the stage to work

// This file is set up for three axes, an LCD display, and a game pad. This requires a 
// Mega as a lot of pins are used. 


//------------------------------------------------------------------------------------------------
// * Enable/disable major OpenStage functions 
//
#define DO_LCD      //Uncomment this line to enable enable LCD character display
#define DO_GAMEPAD  //Uncomment this line to enable PS3 DualShock as an input device
#define PCB         //This is uncommented if the user has an OpenStage PCB


//------------------------------------------------------------------------------------------------
// * Serial communications
//
// You have three options for serial comms: 
// 1) Control stage via PC serial port and receive optional debug information via USB (virtual 
//    serial port). The latter is available by the verbose option in some of the functions. 
// 2) Control stage via USB (virtual serial) but receive no debug info. 
// 3) Disable serial comms for stage control. 
//
// These three possibilities are controlled by altering the following two variables:
#define DO_SERIAL_INTERFACE //Uncomment to enable serial interface
bool controlViaUSB=0;       //Set to 1 to control via USB.

//If using PC serial port, this is the ID of the MEGA's hardware serial line (e.g. Serial3)
//If using an Uno, or another mic with no hardware serial, then this should be set to "Serial"
#define HARDWARE_SERIAL_PORT Serial3
HardwareSerial* SerialComms;  //pointer to stage comms serial object

//The following is not a user setting 
#ifdef DO_SERIAL_INTERFACE
 bool doSerialInterface=1; //Do not alter this value 
#endif

#ifndef DO_SERIAL_INTERFACE
 bool doSerialInterface=0; //Do not alter this value 
#endif





//------------------------------------------------------------------------------------------------
// * Microscope axis hardware definitions. 
//
//                                   === WARNING ===
//   ******************************************************************************
//  ==> This section must be filled out correctly or you may damage your hardware <==
//   ******************************************************************************
//
//
// The properties of each axis are defined as separate variables (mostly arrays with a length 
// equal to the number of axes). You can have up 4 axes. 

const byte numAxes=3; //Set this to the number of axes on you system (values 1 to 4 are possible)


// There are up to four steppers that can be added. The step size, gear ratio, etc can 
// be different on different axes. The arrays that follow specify the properties of the steppers
// on each axis. You can choose which of these axes to enable by commenting or uncommenting the
// definitions below. 
#define AXIS_1
#define AXIS_2
#define AXIS_3
//#define AXIS_4


// gearRatio
// Micrometer gear ratios on X,Y,Z in microns per revolution.
// NOTE: in this case and all others, unused axes can have any value. Values of unused axes
// are simply not read.  
unsigned short gearRatio[maxAxes]={635,635,250,635}; 


// fullStep
// Stepper motor full step size (in degrees) for X,Y,Z. We have tested 1.8 degree and 0.9
// degree step sizes. Motors with finer step sizes are available but driving them in 
// quickly using sub-micron steps is a limiting factor. If you want to get up and running 
// in the shortest time, 0.9 degree motors are suggested. 
float fullStep[maxAxes]={0.9,0.9,0.9,0.9}; //In degrees

// disableWhenStationary
// bool to tell the system whether or not a motor should be disabled when the stage isn't moving.
// Disabling will reduce noise but can cause the motors to move to the nearest full step when the
// power is switched off. Perhaps it makes make sense to do this in X and Y but not Z. 
bool disableWhenStationary[maxAxes]={0,0,0,0};












//------------------------------------------------------------------------------------------------
// PS3 Controller speed settings
// The following settings define how the PS3 controller will control the stage. If you don't have a
// PS3 controller, you can ignore the following 

// * Speed modes (hat-stick)
//
// There will be four (coarse to fine) speeds which may be selected via the two shoulder buttons 
// (L1 and R1). The currently selected speed will be inidicated by the 4 LEDs on the DualShock.
// 1 is fine and slow and 4 is coarse and fast. Here we define the step size and max speed for those
// 4 speed settings. If you change these, you should verify with an osciloscope and the serial 
// monitor that the right values are being produced. You will also need to verify that you are not
// over-driving you motor and causing it to miss steps. Missing steps means the controller will lose
// its absolute position (there is no feedback from the motors). Note that the selection of speed
// values and step sizes are chosen based on the resulting step frequencies the controller must 
// produce and on resonances the motors might exhibit.   
unsigned short maxSpeed[4]={3.5,25,100,750}; //defined in microns per second


// stepSize
// The microstep sizes for each speed mode.
float stepSize[4]={1/16.0, 1/8.0, 1/4.0, 1/2.0}; //Defined in fractions of a full step

// * Speed mode (D-pad)
//
// The D-pad will be used for making fixed-distance motions of a high speed. The size of the motions
// depends on the coarseFine setting and is defined by the DPadStep array. There's a trade-off between
// speed and accuracy. For these fast motions, I'd like to be hit about 1000 um/s but the AccelStepper 
// moveTo function can only churn out about 4.3 kHz on an Arduino Mega. At 1/4 steps we get reliable
// motions and about 700 um/s. A 1/4 step gives us a 0.156 micron resolution in Z (0.9 degree stepper 
// and 250 um per rev micrometer). The motors MUST be enabled throughout or they will slip and become
// hopelessly lost. To get increased accuracy *and* higher speeds we would need a faster micro-controller,
// or write our own hardware-timer based routines, or slave comercial controllers.
float DPadStep[4]={3,5,10,50}; 
float DPadStepSize=1/2.0;
// Acceleration in X, Y, and Z
unsigned long DPadAccel[maxAxes]={1.0E4, 1.0E4, 1.0E4, 1.0E4};


// * moveTo speeds
//
// The moveToTarget() function is executed when the user travels to a right-button set point
// or responds to a serial command. It does this using the settings described below. The minimum
// step size and motor RPM are reported to the serial terminal on bootup. Keep speeds below
// stalling value. Also, remember that the AccelStepper library won't produce pulse rates above
// about 4 kHz.
float moveToStepSize=1.0/2.0;
unsigned int moveToSpeed[maxAxes]={1600,1600,1200,1600}; 
unsigned int moveToAccel[maxAxes]={1.0E4,1.0E4,1.0E4,1.0E4};

// * Allow for inverting of hat-stick motions
// to invert hat-stick motion direction set to -1, otherwise set to 1. 
short hatInvert[maxAxes]={1,1,1,1};


//---------------------------------UNLIKELY TO NEED TO CHANGE THESE-------------------------------
// The following settings can be changed, but you're unlikely to need to do so. 
byte coarseFine=2; //boot up in a fine mode
short hatStickThresh=40; //Ensure we don't get motion for stick values smaller than the following threshold

// curve
// Curve is the non-linear mapping value to convert analog stick position to speed. The idea
// is to make the conversion from analog stick value to motor pulse rate logarithmic. 
// 0 is linear. See the fscale function for details. 
float curve[4]={-7,-6,-5,-4};


//Create wired connection to PS3 gamepad on USB host shield. If you were to attempt a wireless (bluetooth)
//connection you'd want to edit the following code.  
//#include <PS3USB.h>
#ifdef DO_GAMEPAD
 USB Usb;
 PS3USB PS3(&Usb); 
#endif










//IF YOU HAVE AN OPENSTAGE PCB YOU WILL CHANGE NONE OF THE FOLLOWING. 




//------------------------------------------------------------------------------------------------
// * Outputs
// The following are pin definitions of controller outputs. These signal information to the user

byte beepPin=A15; //Set this to the pin to which the Piezo buzzer is connected 

// stageLEDs
// LEDs will light when the stage moves or an axis is reset, 
// *NOTE: Updating the stage LEDs for hat-stick motions requires fast digital writes as motor speed
//        is set in a closed-loop based on hat-stick position. So we set the stage LEDs using 
//        direct port writes. The code expects the LEDS to be on the first 3 pins of the port. 
byte stageLEDs[4]={A0,A1,A2,A3};


// Define pins for LCD display (http://learn.adafruit.com/character-lcds/wiring-a-character-lcd)
#ifdef DO_LCD
   LiquidCrystal lcd(A6,A7,A11,A12,A13,A14);
#endif


//------------------------------------------------------------------------------------------------
// * Motor control DIO lines
// Alter the following based on how your system is wired. 

// stepOut
// One pulse at these pins moves the motor by one step (or one micro-step)
byte stepOut[maxAxes]={44,31,47,28}; //Set these to the step out pins (ordered X, Y, Z, Z')

// stepDir
// These pins tell the Big Easy Driver to which they connect which direction to rotate the motor
byte stepDir[maxAxes]={45,30,46,29}; //Ordered X, Y, Z, Z'

// enable
// If these pins are low, the motor is enabled. If high it's disabled. Disabling might decrease 
// electrical noise but will lead to errors in absolute positioning. 
byte enable[maxAxes]={39,36,7,23}; //Ordered X, Y, Z, Z' 

// The microstep pins.
// These pins define the microstep size. The MS pins on all axes are wired together.

//Let's define an array with the microstepping pins
byte MS[4][3]={ 
	{42,43,40},  //channel 1, MS pins 1,2,3
	{33,32,35},  //channel 2, MS pins 1,2,3
	{49,48,10},  //channel 3, MS pins 1,2,3
	{26,27,24}   //channel 4, MS pins 1,2,3
	};

// Do not edit the following lines
// * AccelStepper  
// Set up AccelStepper instances 
bool axisPresent[maxAxes]={0,0,0,0}; //Don't even edit this line 
AccelStepper *mySteppers[numAxes];

#ifdef AXIS_1
 AccelStepper stepper1(1, stepOut[0], stepDir[0]); 
#endif

#ifdef AXIS_2
 AccelStepper stepper2(1, stepOut[1], stepDir[1]); 
#endif

#ifdef AXIS_3
 AccelStepper stepper3(1, stepOut[2], stepDir[2]); 
#endif

#ifdef AXIS_4
 AccelStepper stepper4(1, stepOut[3], stepDir[3]); 
#endif

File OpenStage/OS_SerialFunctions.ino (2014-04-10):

//------------------------------------------------------------------------------------------------
// This file contains functions necessary for controlling OpenStage via the serial port


//------------------------------------------------------------------------------------------------
//Based on code from The Arduino Cookbook, M. Margolis, recipe 4.5
//read CSV from serial port and store in the global array values
//ADD ERROR CHECKING IF TOO MANY OR TOO FEW VALUES ARE SENT
int readSerialCSV(){
  int fieldIndex = 0;  // the current field being received
  int sSign[numAxes]={1,1,1}; //sign 

  char ch;
  while (ch != '$'){ //read until the terminator ($) is reached
     if (SerialComms->available()){
         ch = SerialComms->read();
      }else{
         continue;
      }

    // is this an ASCII digit between 0 and 9?
    if(ch >= '0' && ch <= '9'){
      // yes, accumulate the value if the fieldIndex is within range
      // additional fields are not stored
      if(fieldIndex < numAxes)
        values[fieldIndex] = (values[fieldIndex] * 10) + (ch - '0'); 
      } else if (ch == '-') { //deal with negative numbers
        if(fieldIndex < numAxes)
          sSign[fieldIndex] = -1;        
      } else if (ch == ',') {  // comma is our separator, so move on to the next field
         fieldIndex++;   // increment field index 
     }
   }
   
   //set the signs
   for (byte ii=0; ii<fieldIndex+1; ii++)
      values[ii]=values[ii]*sSign[ii];
     
   return fieldIndex;
}

//------------------------------------------------------------------------------------------------
//Make a relative or absolute motion 
void serialMove()
{
   //Determine if this will be an absolute or relative motion
   while(SerialComms->available() == 0 );//block until char arrives
   char moveType=SerialComms->read();
    
   //Define variables
   int doneReading=0; //1 when all axis fields have been read


   float serialTarget[numAxes]; //Where we will be going to in microns
   
   int fieldIndex=readSerialCSV();

   //Determine where to move [**IS THIS MIN STUFF RIGHT?**]
   for (byte ii=0; ii<min(numAxes, fieldIndex+1); ii++){
      if (moveType=='r')
          serialTarget[ii]=stagePosition[ii]+values[ii]/1.0E3;
        if (moveType=='a') 
          serialTarget[ii]=values[ii]/1.0E3; //because least sig digits are after decimal point
          values[ii] = 0; // set the values to zero, ready for the next message
     }

    moveToTarget(serialTarget);
    SerialComms->print('$'); //send a dollar, which is the terminator
 
} //End serialRelativeMove()



//------------------------------------------------------------------------------------------------
// * serialSetMode
// Set speed mode on the DualShock
void serialSetMode(){
  if (!doGamePad){
    return;
  }

  while(SerialComms->available() == 0 );//block until char arrives

  char ch = SerialComms->read();
      
   if (ch=='1')
     coarseFine=1;
   if (ch=='2')
     coarseFine=2;
   if (ch=='3')
     coarseFine=3;
   if (ch=='4')
     coarseFine=4;
     
   setPSLEDS();
} //End serialSetMode()


//------------------------------------------------------------------------------------------------
// * zero stage
// Current position becomes the new zero. 
// Also updates any stored locations so that we can still returns to them
void zeroStage(){
  float delta[numAxes]; //difference between current position and previous zero
  for (byte ii=0; ii<numAxes; ii++){
    delta[ii]=stagePosition[ii];
    stagePosition[ii]=0;
    lcdStagePos(ii,stagePosition[ii],0);
  }  
  
  for (byte ii=0; ii<4; ii++){
    if (locationStored==0)
       continue;       
    for (byte jj; jj<numAxes; jj++)
      buttonStageLocations[jj][ii]=buttonStageLocations[jj][ii]-delta[ii];
  }
   
     
} //End zeroStage()


//------------------------------------------------------------------------------------------------
// * tell position
// Report the current stage position via the serial port
void tellPosition(){

  for (byte ii=0; ii<numAxes; ii++){
    SerialComms->print(stagePosition[ii]);
    if (ii<numAxes-1)
      SerialComms->print(",");
  }
  
  SerialComms->print("$");
     
} //End tell position
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

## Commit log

2014-04-08 Add example Python and MATLAB serial control functions. Move Arduino (firmware) functions into their own directory.
2014-04-10 Don't print verbose information to USB if USB is being used to control stage.
2014-04-10 Remove USB serial print that was orphaned from some previous debugging attempt.
2014-04-10 controlling stage via USB is now verified to work
2014-04-10 Modify MATLAB stage goto function to cope with arbitrary numbers of axes.
2014-04-10 Largely working but takes a step each time it receives a serial port command. So if you repeatedly ask to go to the current position, the motor pulses along.
2014-04-12 Beep and report connection when MATLAB first links to stage.
2014-04-13 Improve build instructions for stage.
2014-04-17 Let's not mess with pin 13 by default
2014-04-18 Clarify that increasing current can reduce top speed.
2014-05-15 Begin modifying code to accommodate the new PCB.
2014-05-29 Set up PCB settings file.
2014-05-29 Add build instructions for PCB. Instructions also contain an outline for how to set up OpenStage, use the controller, MATLAB interfacing, and how to avoid motor skips, etc.
2014-05-30 Add parts list for PCB build.
2014-06-03 Highlight the importance of not ripping up traces on the Quadstepper when removing the power jack.
2014-06-04 Changes to getInfo message sent by stage to PC.
2014-06-04 Explain issues with stage speed.
2014-10-08 Highlight that it's the *stage* we're building.
2015-04-20 Update README.md
    pcb info
2015-09-21 Add missing variables to non-PCB settings files.
2015-10-03 Add PCB files. These files should be for the corrected version (LCD and serial port not inverted).
    [OpenStage.GBL, OpenStage.GBO, OpenStage.GBS, OpenStage.GTL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]
2017-07-11 add CAD files for thimble to shaft connection
    [motor_coupler.ipt, stage_assy_micrometer_coupler.ipt]
2021-01-18 Replace quad-stepper board
    [OpenStage.sch]
2021-01-18 Generate gerbers for new PCB
    [OpenStage.GBL, OpenStage.GBO, OpenStage.GBS, OpenStage.GTL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]
2021-01-25 mention new PCB

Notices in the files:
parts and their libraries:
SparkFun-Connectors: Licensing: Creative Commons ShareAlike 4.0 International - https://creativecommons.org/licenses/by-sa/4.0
